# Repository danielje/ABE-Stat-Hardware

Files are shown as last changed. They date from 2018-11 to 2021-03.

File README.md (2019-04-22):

# ABE-Stat-Hardware
ABE-Stat Hardware Design / Assembly Files
For Android source code for wireless interface for device, go to https://github.com/danielje/ABE-Stat
For firmware source code (Arduino IDE) go to https://github.com/danielje/ABE-Stat-Arduino

Comprehensive documentation for the project is available in the open-source publication here: http://jes.ecsdl.org/content/166/9/B3056.short This set of files is referred to as "Files S1" in the manuscript above.

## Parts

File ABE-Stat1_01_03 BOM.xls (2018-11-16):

 | Bill of Materials for pc board: "ABE-Stat 1_01_03" as of: 5/11/2018 12 PM
Ref | Item | Quantity | for 50 | w overage | Designator | Description | Value | Package | Type | Manufacturer | Mfctr. Part Number | Distributor | Dstbr. Part # | Cost Each | Total parts cost | Incl. In Kit | Need for Build | Qty. To Return | Comments
PSTAT1 | 1 | 1 | 50 | 60 | A1 | ESP8266 WiFi Module |  |  |  | Esspressif | ESP-12S | Adafruit; Electrodragon | ESP-12S | $2.00 |  | ($2 from electrodragon; $6.95 from Adafruit)
PSTAT2 | 2 | 1 | 50 | 60 | A2 | MODULE BLUETOOTH V2.1+EDR |  |  | smt | Microchip Technology (http://digikey.com/Suppliers/us/Microchip-Technology.page?lang=en) | RN-42 | Digikey | 740-1038-1-ND | $15.44 | $15.44
PSTAT3 | 3 | 17 | 850 | 950 | C1 - C17 | CAP CER 0.1UF 16V X7R 0805 | 0.1 uF | 0805 | smt | Johanson Dielectrics Inc. | 160R15W104KV4T | Digikey | 709-1183-1-ND | $0.06 | $0.94
PSTAT4 | 4 | 9 | 450 | 550 | C18 - C26 | CAP CER 10UF 16V 20% X5R 0805 | 10 uF | 0805 | smt | TDK Corporation (http://digikey.com/Suppliers/us/TDK.page?lang=en) | C2012X5R1C106M085AC | Digikey | 445-7645-1-ND | $0.06 | $0.57
PSTAT5 | 5 | 4 | 200 | 300 | C27 - C30 | CAP CER 2200PF 50V X7R 0805 | 2200pF | 0806 | smt | KEMET (https://www.digikey.com/en/supplier-centers/k/kemet) | C0805C222K5RACTU | Digikey | 399-1151-1-ND | $0.01
PSTAT6 | 6 | 3 | 150 | 250 | C31 - C33 | CAP CER 10000PF 16V X7R 0805 | 10000 pF | 0805 | smt | KEMET | C0805C103K4RACTU | Digikey | 399-7995-1-ND | $0.03 | $0.10
PSTAT7 | 7 | 3 | 150 | 250 | C34 - C36 | CAP CER 4.7UF 10V X7R 0805 | 4.7 uF | 0805 | smt | TDK Corporation | C2012X7R1A475M085AC | Digikey | 445-14528-1-ND | $0.08 | $0.23
PSTAT8 | 8 | 2 | 100 | 200 | C37, C38 | CAP CER 0.22UF 16V X7R 0805 | 0.22 uF | 0805 | smt | Yageo | CC0805JRX7R7BB224 | Digikey | 311-4267-1-ND | $0.04 | $0.08
PSTAT9 | 9 | 1 | 50 | 150 | C39 | CAP CER 10PF 50V C0G/NP0 0805 | 10 pF | 0805 | smt | KEMET | C0805C100J5GACAUTO | Digikey | 399-6914-1-ND | $0.02 | $0.02
PSTAT10 | 10 | 1 | 50 | 75 | C40 | CAP ALUM POLY 47UF 20% 6.3V SMD | 47 uF | 7343 | smt | Panasonic Electronic Components (https://www.digikey.com/en/supplier-centers/p/panasonic) | EEF-CD0J470R | Digikey | PCE3160CT-ND | $0.53 | $0.53
PSTAT11 | 11 | 2 | 100 | 200 | D1, D2 | DIODE SCHOTTKY 40V 1A SOD123 |  | SOD123 | smt | Nexperia USA Inc. (https://www.digikey.com/en/supplier-centers/n/nexperia) | PMEG4010CEGWX | Digikey | 1727-7337-1-ND | $0.12 | $0.24
PSTAT12 | 12 | 6 | 300 | 400 | FB1 - FB3 | FERRITE BEAD 1.5 KOHM 0805 1LN |  | 0805 | smt | Wurth Electronics Inc. (https://www.digikey.com/en/supplier-centers/w/wurth-electronics) | 742792097 | Digikey | 732-4649-1-ND | $0.19 | $1.16
PSTAT13 | 13 | 1 | 50 | 60 | J1 | CONN TERM BLK 5POS 2.5MM SMD |  |  | smt | Phoenix Contact (https://www.digikey.com/en/supplier-centers/p/phoenix-contact) | 1771127 | Digikey | 277-2075-1-ND | $0.93 | $0.93
PSTAT14 | 14 | 1 | 50 | 60 | J2 | CONN TERM BLK 2POS 2.5MM SMD |  |  | smt | Phoenix Contact (https://www.digikey.com/en/supplier-centers/p/phoenix-contact) | 1771091 | Digikey | 277-2072-1-ND | $0.65 | $0.65
PSTAT15 | 15 | 1 | 50 | 60 | J3 | CONN RCPT USB MICRO B R/A SMT |  |  | smt | Wurth Electronics Inc. (https://www.digikey.com/en/supplier-centers/w/wurth-electronics) | 629105136821 | Digikey | 732-3155-1-ND | $1.11 | $1.11
PSTAT16 | 16 | 1 | 50 | 60 | J4 | CONN HEADER PH SIDE 2POS 2MM SMD |  |  | smt | JST Sales America Inc. | S2B-PH-SM4-TB(LF)(SN) | Digikey | 455-1749-1-ND | $0.42
PSTAT17 | 17 | 1 | 50 | 60 | J5 | 06 SIL VERT SMT HDR 450/RL |  |  | smt | Harwin Inc. | M20-8770642R | Digikey | 952-3487-1-ND | $0.52 | $0.52
PSTAT18 | 18 | 2 | 100 | 120 | LED1, LED2 | LED RED CLEAR 1206 SMD |  | 1206 | smt | QT Brightek (QTB) (https://www.digikey.com/en/supplier-centers/q/qt-brightek) | QBLP651-R | Digikey | 1516-1172-1-ND | $0.22 | $0.43
PSTAT19 | 19 | 1 | 50 | 60 | LED3 | LED RGB CLEAR 1411 SMD |  |  | smt | Wurth Electronics Inc (http://www.digikey.com/Suppliers/us/Wurth-Electronics.page?lang=en) | 150141M173100 | DigiKey | 732-4998-1-ND | $0.60 | $0.60
PSTAT20 | 20 | 5 | 250 | 275 | Q1 - Q5 | MOSFET N-CH 50V 220MA SOT-23 |  | SOT-23-3 | smt | Fairchild Semiconductor (http://digikey.com/Suppliers/us/Fairchild-Semiconductor.page?lang=en) | BSS138 | Digikey | BSS138CT-ND | $0.04 | $0.21
PSTAT21 | 21 | 1 | 50 | 75 | Q6 | MOSFET P-CH 50V 130MA SOT323 |  | SOT-23-3 | smt | Diodes Incorporated | BSS84W-7-F | Digikey | BSS84W-FDICT-ND | $0.12 | $0.12
PSTAT22 | 22 | 3 | 150 | 175 | Q7 - Q9 | MOSFET P-CH 8V 1.4A SOT-323 |  |  |  | ON Semiconductor | NTS2101PT1G | Digikey | NTS2101PT1GOSCT-ND | $0.17 | $0.50
PSTAT23 | 23 | 20 | 1000 | 1100 | R1 - R20 | RES 10K OHM 1/8W 5% 0805 SMD | 10 k | 0805 | smt | Panasonic Electronic Components (http://digikey.com/Suppliers/us/Panasonic-Electronic-Components.page?lang=en) | ERJ-6GEYJ103V | Digikey | P10KACT-ND | $0.00448 | #REF!
PSTAT24 | 24 | 6 | 300 | 400 | R20 - R26 | RES SMD 1K OHM 5% 1/8W 0805 | 1 k | 0805 | smt | Panasonic Electronic Components (http://digikey.com/Suppliers/us/Panasonic-Electronic-Components.page?lang=en) | ERJ-6GEYJ102V | Digikey | P1.0KACT-ND | $0.0041
PSTAT25 | 25 | 4 | 200 | 300 | R27 - R30 | RES SMD 22K OHM 5% 1/8W 0805 | 22k | 0805 | smt | Panasonic Electronic Components (http://digikey.com/Suppliers/us/Panasonic-Electronic-Components.page?lang=en) | ERJ-6GEYJ223V | Digikey | P22KACT-ND | $0.0041
PSTAT26 | 26 | 4 | 200 | 300 | R31 - R34 | RES SMD 100K OHM 0.1% 1/8W 0805 | 100k | 0805 | smt | Panasonic Electronic Components | ERA-6AEB104V | Digikey | P100KDACT-ND | $0.05
PSTAT27 | 27 | 3 | 150 | 250 | R35 - R37 | RES SMD 3.3K OHM 5% 1/8W 0805 | 3.3k | 0805 | smt | Panasonic Electronic Components (http://digikey.com/Suppliers/us/Panasonic-Electronic-Components.page?lang=en) | ERJ-6GEYJ332V | Digikey | P3.3KACT-ND | $0.0041
PSTAT28 | 28 | 3 | 150 | 250 | R38 - R40 | RES SMD 10K OHM 0.1% 1/8W 0805 | 10k | 0805 | smt | Panasonic Electronic Components | ERA-6AEB103V | Digikey | P10KDACT-ND | $0.05
PSTAT29 | 29 | 2 | 100 | 200 | R41, R42 | RES SMD 1M OHM 0.1% 1/8W 0805 | 1M | 0805 | smt | Panasonic Electronic Components | ERA-6AEB105V | Digikey | P1MDACT-ND | $0.05
PSTAT30 | 30 | 2 | 100 | 200 | R43, R44 | RES SMD 100 OHM 5% 1/8W 0805 | 100W | 0805 | smt | Panasonic Electronic Components (http://digikey.com/Suppliers/us/Panasonic-Electronic-Components.page?lang=en) | ERJ-6GEYJ101V | Digikey | P100ACT-ND | $0.0041
PSTAT31 | 31 | 1 | 50 | 150 | R45 | RES SMD 1K OHM 0.1% 1/8W 0805 | 1k | 0805 | smt | Panasonic Electronic Components (https://www.digikey.com/en/supplier-centers/p/panasonic) | ERA-6AEB102V | Digikey | P1.0KDACT-ND | $0.05
PSTAT32 | 32 | 1 | 50 | 150 | R46 | RES SMD 2K OHM 5% 1/8W 0805 | 2k | 0805 | smt | Panasonic Electronic Components (https://www.digikey.com/en/supplier-centers/p/panasonic) | ERJ-6GEYJ202V | Digikey | P2.0KACT-ND | $0.01
PSTAT33 | 33 | 1 | 50 | 150 | R47 | RES SMD 33K OHM 5% 1/8W 0805 | 33k | 0805 | smt | Panasonic Electronic Components (https://www.digikey.com/en/supplier-centers/p/panasonic) | ERJ-6GEYJ333V | Digikey | P33KACT-ND | $0.0041
PSTAT34 | 34 | 1 | 50 | 100 | R48 | RES SMD 2 OHM 5% 1W 2512 | 2W | 2512 | smt | Panasonic Electronic Components (https://www.digikey.com/en/supplier-centers/p/panasonic) | ERJ-1TYJ2R0U | Digikey | PT2.0XCT-ND | $0.07
PSTAT35 | 35 | 3 | 150 | 160 | S1 - S3 | SWITCH PUSH SPST-NO 0.1A 35V |  |  | smt | RAFI USA (https://www.digikey.com/en/supplier-centers/r/rafi) | 1.14002.1010000 | Digikey | 1.14002.1010000CT-ND | $0.06
PSTAT36 | 36 | 1 | 50 | 60 | SH1 | BOARD LEVEL EMI SHIELD 1.15"x2.9"x0.1" |  |  | smt | Orbel | G-1.15SA2.9-0.1ZC | Orbel | G-1.15SA2.9-0.1ZC | $5.00 | $5.00
PSTAT37 | 37 | 1 | 50 | 60 | U1 | IC CONTROLLR LI-ION 4.2V SOT23-5 |  | SOT23-5 | smt | Microchip Technology (https://www.digikey.com/en/supplier-centers/m/microchip-technology) | MCP73831T-2ACI/OT | Digikey | MCP73831T-2ACI/OTCT-ND | $0.43
PSTAT38 | 38 | 1 | 50 | 60 | U2 | IC REG LDO 3.3V 0.6A SOT-2233L |  | SOT-2233L | smt | Diodes Incorporated (https://www.digikey.com/en/supplier-centers/d/diodes) | AP7365-33EG-13 | Digikey | AP7365-33EG-13DICT-ND | $0.39
PSTAT39 | 39 | 1 | 50 | 60 | U3 | IC VREF SERIES 3.3V SOT23-3 | 3.3V | SOT-23-3 | smt | Intersil (https://www.digikey.com/en/supplier-centers/i/intersil) | ISL60002BAH333Z-T7A | Digikey | ISL60002BAH333Z-T7ACT-ND | $4.72
PSTAT40 | 40 | 1 | 50 | 60 | U4 | IC VREF GND REF ADJ 8SOIC |  | 8SOIC | smt | Texas Instruments | TLE2426IDR | Digikey | 296-1345-1-ND | $0.79
PSTAT41 | 41 | 2 | 100 | 110 | U5, U6 | IC SHIFT REGISTER 8-BIT 16-TSSOP |  | 16-TSSOP | smt | Fairchild/ON Semiconductor (https://www.digikey.com/en/supplier-centers/f/fairchild) | MM74HC595MTCX | Digikey | MM74HC595MTCXCT-ND | $0.15
PSTAT42 | 42 | 2 | 100 | 110 | U7, U8 | IC MUX/DEMUX 2X1 8VSSOP |  | 8VSSOP | smt | Nexperia USA Inc. (https://www.digikey.com/en/supplier-centers/n/nexperia) | 74LVC1G53DC,125 | Digikey | 1727-3492-1-ND | $0.17
PSTAT43 | 43 | 2 | 100 | 110 | U9, U10 | IC SWITCH SPDT SC70-6 |  | SC-70-6 | smt | Analog Devices Inc. (https://www.digikey.com/en/supplier-centers/a/analog-devices) | ADG779BKSZ-REEL7 | Digikey | ADG779BKSZ-REEL7CT-ND | $1.00
PSTAT44 | 44 | 1 | 50 | 60 | U11 | NETWORK ANALYZER 12B 1MSP 16SSOP |  | 16SSOP | smt | Analog Devices Inc. | AD5933YRSZ-REEL7 | Digikey | AD5933YRSZ-REEL7CT-ND | $34.16
PSTAT45 | 45 | 1 | 50 | 60 | U12 | IC ADC 24-BIT 2KSPS 16-TSSOP |  | 16-TSSOP | smt | Analog Devices Inc. | ADS1220IPWR | Digikey | 296-39851-1-ND | $7.87
PSTAT46 | 46 | 1 | 50 | 60 | U13 | IC DAC 16BIT SPI/SRL SOT23-8 |  | SOT23-8 | smt | Analog Devices Inc. | AD5061BRJZ-2REEL7 | Digikey | AD5061BRJZ-2REEL7CT-ND | $6.40
PSTAT47 | 47 | 1 | 50 | 60 | U14 | IC SWITCH OCTAL SPST 24TSSOP |  | 24TSSOP | smt | Analog Devices Inc. | ADG715BRUZ | Digikey | ADG715BRUZ-REEL7CT-ND | $5.20
PSTAT48 | 48 | 1 | 50 | 60 | U15 | IC GATE XOR 2CH 2-INP US8 | XOR | US8 | smt | Texas Instruments (http://digikey.com/Suppliers/us/Texas-Instruments.page?lang=en) | SN74LVC2G86DCUR | Digikey | 296-13275-1-ND | $0.28 | $0.84
PSTAT49 | 49 | 1 | 50 | 60 | U16 | IC MULTIPLEXER 4X1 10USOIC |  | 10USOIC | smt | Analog Devices Inc. | ADG704BRMZ | Digikey | ADG704BRMZ-REELCT-ND | $1.41
PSTAT50 | 50 | 1 | 50 | 60 | U17 | IC AMP PREC 3FA BIAS CURR 8SOIC |  | 8SOIC | smt | Texas Instruments (http://digikey.com/Suppliers/us/Texas-Instruments.page?lang=en) | LMP7721MA/NOPB | Digikey | LMP7721MA/NOPB-ND | $5.29 | $10.57
PSTAT51 | 51 | 3 | 150 | 160 | U18 - U20 | IC OPAMP GP 2.5MHZ RRO 8VSSOP |  | 8-MSOP | smt | Texas Instruments | LMP7702MM/NOPB | Digikey | LMP7702MM/NOPBCT-ND | $2.61
PSTAT52 | 52 | 2 | 100 | 110 | U21, U22 | IC OPAMP GP 17MHZ RRO SOT23-5 |  | SOT23-5 | smt | Texas Instruments | LMP7715MF/NOPB | Digikey | LMP7715MF/NOPBCT-ND | $1.22
PSTAT53 | 53 | 1 | 50 | 60 | X1 | OSC MEMS 250.0000KHZ CMOS SMD | 250kHz | 4-SMD | smt | Microchip Technology | DSC6083CI2A-250K000 | Digikey | DSC6083CI2A-250K000T-ND | $0.69
 |  | 142

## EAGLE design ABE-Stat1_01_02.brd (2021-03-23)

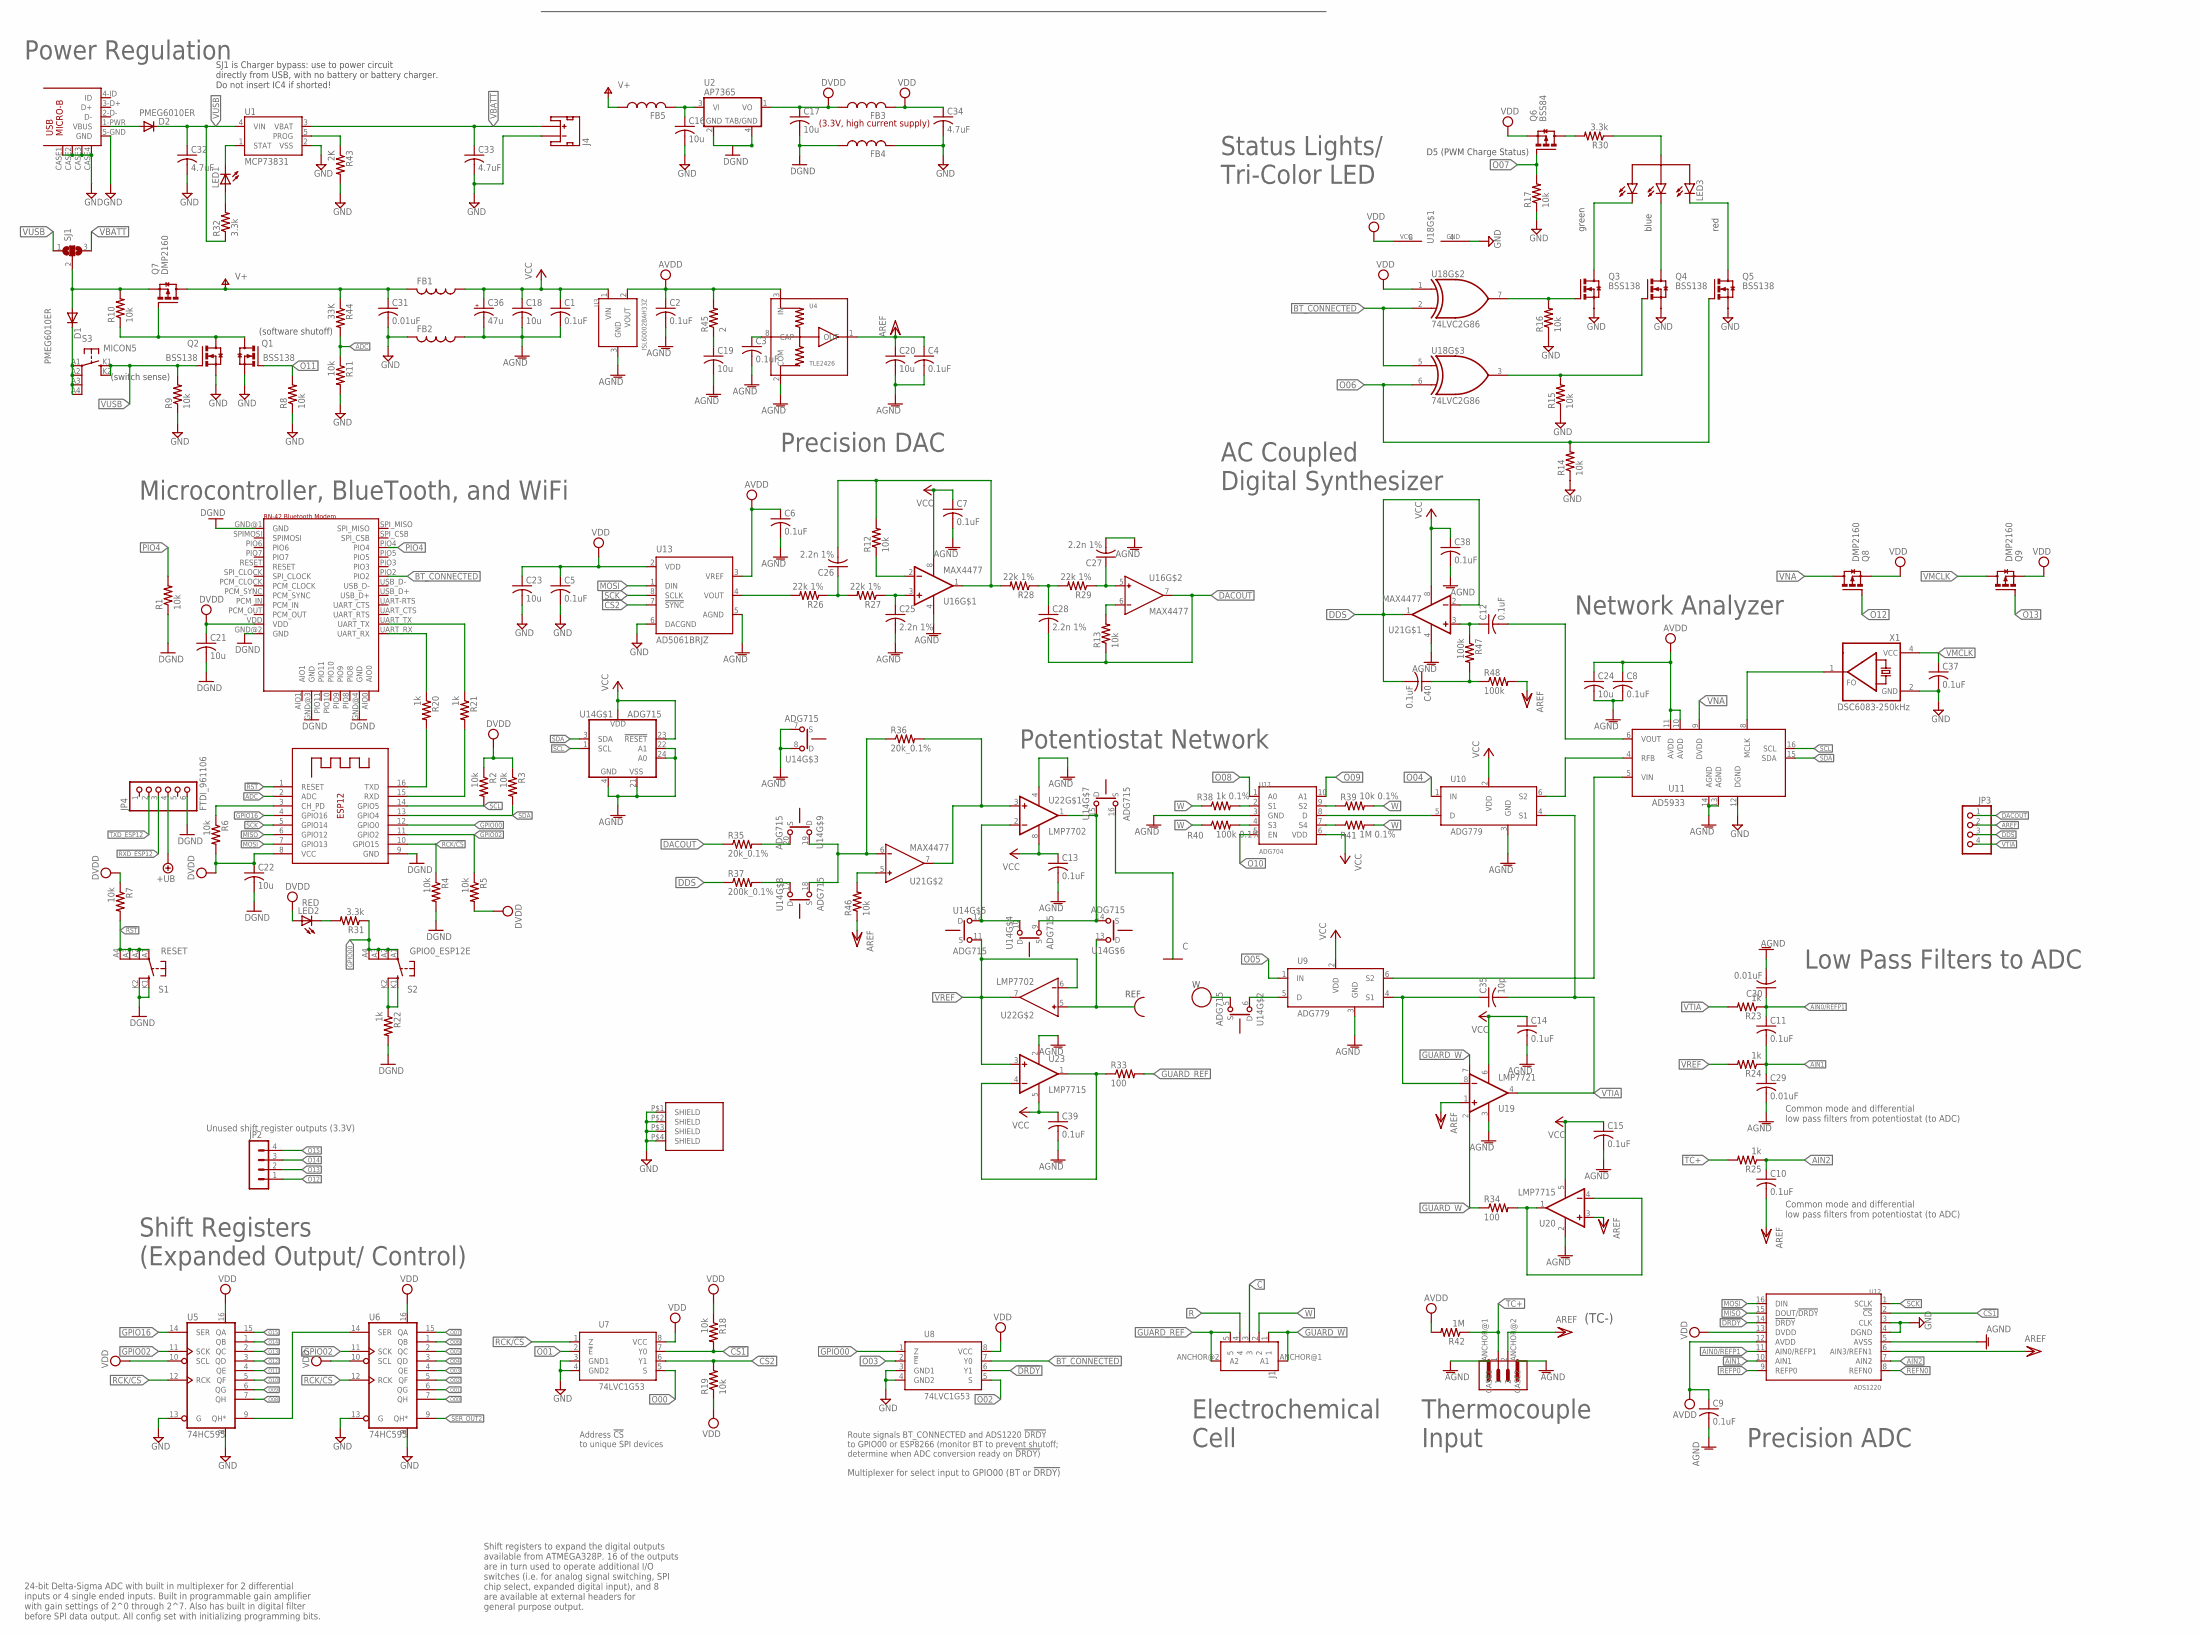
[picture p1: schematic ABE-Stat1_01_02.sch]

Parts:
A1: ESP-12E; ESP-12
A2: RN-42_BLUETOOTH; RN-42
C1, C2, C3, C4, C5, C6, C7, C8, C9, C10, C11, C12, C13, C14, C15, C37, C38, C39, C40: 0.1uF; C0805
C16, C17, C18, C19, C20, C21, C22, C23, C24: 10u; C0805
C25, C26, C27, C28: 2.2n 1%; C0805
C29, C30, C31: 0.01uF; C0805
C32, C33, C34: 4.7uF; C0805
C35: 10p; C0805
C36: 47u; D/7343-31W
D1, D2: PMEG6010ER; DIODE_SOD123
FB1, FB2, FB3, FB4, FB5: FERRITE_BEAD_5A_0805; R0805
J1: 5-PIN-VERTICAL-PHOENIX_2.5MM-SMD; 5-PIN-VERT_PHOENIX_SMD
J2: 1A_JENKINS_2013_2PIN_SMD_PHOENIX_CONTACTVERTICAL; 2-PIN-VERT_PHOENIX_SMD
J3: USB-MICRO-B; USB_MICRO_B_WURTH_629105136821
J4: JST_2MM_MALE; JST-2-SMD
JP2: MA04-1
JP3: PINHD-1X4; 1X04
JP4: FTDI_961106; 6_PIN_0.1IN_STRAIGHT_HEADER
LED1: LEDCHIPLED_1206; CHIPLED_1206
LED2: RED; LED-1206
LED3: LED_RBG_COM_ANODE; LED_RGB_WURTH_150141M173100
Q1, Q2, Q3, Q4, Q5: BSS138; SOT-23
Q6: BSS84; SOT-23-3
Q7, Q8, Q9: DMP2160; SOT-23-3
R1, R2, R3, R4, R5, R6, R7, R8, R9, R10, R11, R12, R13, R14, R15, R16, R17, R18, R19, R46: 10k; R0805
R20, R21, R22, R23, R24, R25: 1k; R0805
R26, R27, R28, R29: 22k 1%; R0805
R30, R31, R32: 3.3k; R0805
R33, R34: 100; R0805
R35, R36: 20k_0.1%; R0805
R37: 200k_0.1%; R0805
R38: 1k 0.1%; R0805
R39: 10k 0.1%; R0805
R40: 100k 0.1%; R0805
R41: 1M 0.1%; R0805
R42: 1M; R0805
R43: 2K; R0805
R44: 33K; R0805
R45: 2; R2512
R47, R48: 100k; R0805
S1: RESET; RAFI-MICON5_SWITCH
S2: GPIO0_ESP12E; RAFI-MICON5_SWITCH
S3: MICON5; RAFI-MICON5_SWITCH
SH1: SMARTDART_SHIELD; SMARTDART-SHIELD
SJ1: SJ2W; SJ_2
U1: MCP73831; SOT23-5
U2: AP7365; SOT-223
U3: ISL60002BAH33Z; SOT-23-3
U4: TLE2426; SOIC-8
U5, U6: 74HC595; TSSOP16
U7, U8: 74LVC1G53; VSSOP8
U9, U10: ADG779; SC70-6
U11: AD5933; SSOP-16
U12: ADS1220; TSSOP16
U13: AD5061BRJZ; SOT-23-8
U14: ADG715; TSSOP24
U16, U21: MAX4477; UMAX8
U17: ADG704; MSOP10
U18: 74LVC2G86; US-8
U19: LMP7721; SOIC-8
U20, U23: LMP7715; SOT23-5
U22: LMP7702; MSOP8
X1: DSC6083-250kHz; DSC60XX_OSCILLATOR_3.2X2.5MM

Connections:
!CS1: R18.2, U7.7 (Y0), U12.2 (!CS)
!CS2: R19.2, U7.6 (Y1), U13.7 (!SYNC)
!DRDY: U8.6 (Y1), U12.14 (!DRDY)
!RST: A1.1 (RESET), R7.2, S1.A1, S1.A2 (P1), S1.A3 (P2), S1.A4 (P3)
+UB: JP4.4
AD5933_VIN: U9.6 (S2), U11.5 (VIN)
ADC: A1.2 (ADC), R11.1, R44.2
AGND: C1.2, C2.2, C3.2, C4.2, C6.2, C7.2, C8.2, C9.2, C13.2, C14.2, C15.2, C18.2, C19.2, C20.2, C24.2, C25.2, C27.2, C29.2, C30.2, C36.-, C38.2, C39.2, FB2.1, J2.ANCHOR@1 (CASE1), J2.ANCHOR@2 (CASE2), U3.3 (GND), U4.2 (COM), U9.3 (GND), U10.3 (GND), U11.13 (AGND), U11.14 (AGND), U12.5 (AVSS), U13.5 (AGND), U14.4 (GND), U14.7 (S), U14.8 (D), U14.21 (VSS), U14.22 (A1), U14.24 (A0), U16.4 (V-), U17.3 (GND), U19.3 (V-), U20.2 (V-), U21.4 (V-), U22.4 (V-), U23.2 (V-)
AIN0/REFP1: C11.1, C30.1, R23.1, U12.11 (AIN0/REFP1)
AIN1: C11.2, C29.1, R24.1, U12.10 (AIN1)
AIN2: C10.1, R25.1, U12.7 (AIN2)
AREF: C4.1, C10.2, C20.1, J2.2, JP3.2, R46.1, R48.2, U4.1 (OUT), U12.6 (AIN3/REFN1), U19.1 (+IN), U20.3 (+IN)
AVDD: C2.1, C6.1, C8.1, C9.1, C24.1, R42.2, R45.2, U3.2 (VOUT), U4.3 (IN), U11.10 (AVDD), U11.11 (AVDD), U12.12 (AVDD), U13.3 (VREF)
BT_CONNECTED: A2.PIO2, U8.7 (Y0), U18.2 (I1), U18.5 (I0)
C: J1.3, U14.16 (S)
DACOUT: C28.2, JP3.1, R13.1, R35.1, U16.7 (OUT)
DDS: C40.2, JP3.3, R37.1, U21.1 (OUT), U21.2 (-IN)
DGND: A1.9 (GND), A2.GND@1 (GND), A2.GND@2 (GND), A2.GND@3 (GND), A2.GND@4 (GND), C17.2, C21.2, C22.2, FB4.1, JP4.6, R1.1, R4.2, R22.2, S1.K1 (S), S1.K2 (S1), U2.2 (GND), U2.4 (GND1)
DVDD: A1.8 (VCC), A2.VDD, C17.1, C21.1, C22.1, FB3.1, LED2.A, R2.1, R3.1, R5.2, R6.2, R7.1, U2.1 (VO)
GND: C5.2, C16.2, C23.2, C31.2, C32.2, C33.2, C34.2, C37.2, FB2.2, FB4.2, J3.5-GND (GND), J3.CASE1 (CASE), J3.CASE2 (CASE), J3.CASE3 (CASE), J3.CASE4 (CASE), J4.1 (-), Q1.2-S (S), Q2.2-S (S), Q3.2-S (S), Q4.2-S (S), Q5.2-S (S), R8.1, R9.1, R11.2, R14.1, R15.1, R16.1, R17.1, R43.2, SH1.P$1, SH1.P$2, SH1.P$3, SH1.P$4, U1.2 (VSS), U5.8 (GND), U5.13 (G), U6.8 (GND), U6.13 (G), U7.3 (GND1), U7.4 (GND2), U8.3 (GND1), U8.4 (GND2), U11.12 (DGND), U12.3 (CLK), U12.4 (DGND), U13.6 (DACGND), U18.4 (GND), X1.2 (GND)
GPIO00: A1.12 (GPIO0), R31.1, S2.A1, S2.A2 (P1), S2.A3 (P2), S2.A4 (P3), U8.1 (Z)
GPIO02: A1.11 (GPIO2), R5.1, U5.11 (SCK), U6.11 (SCK)
GPIO16: A1.4 (GPIO16), U5.14 (SER)
GUARD_REF: J1.5, J1.ANCHOR@2 (A2), R33.2
GUARD_W: J1.1, J1.ANCHOR@1 (A1), R34.1, U19.2 (GUARD), U19.7 (GUARD)
MISO: A1.6 (GPIO12), U12.15 (DOUT/!DRDY)
MOSI: A1.7 (GPIO13), U12.16 (DIN), U13.1 (DIN)
unnamed: A2.UART_RX, R20.1
unnamed: U14.10 (D), U14.12 (D), U22.2 (-IN)
unnamed: D2.A, J3.1-PWR (VBUS)
unnamed: A2.UART_TX, R21.1
unnamed: Q3.1-G (G), R16.2, U18.7 (O)
unnamed: U9.5 (D), U14.6 (D)
unnamed: R43.1, U1.5 (PROG)
unnamed: U5.9 (QH*), U6.14 (SER)
unnamed: C25.1, R27.1, U16.3 (+IN)
unnamed: LED1.C, U1.1 (STAT)
unnamed: R26.2, U13.4 (VOUT)
unnamed: LED1.A, R32.2
unnamed: C19.1, R45.1
unnamed: R37.2, U14.17 (D)
unnamed: C26.1, R26.1, R27.2
unnamed: R22.1, S2.K1 (S), S2.K2 (S1)
unnamed: Q4.1-G (G), R15.2, U18.3 (O)
unnamed: D1.C, S3.A1, S3.A2 (P1), S3.A3 (P2), S3.A4 (P3)
unnamed: C3.1, U4.8 (CAP)
unnamed: C26.2, R12.2, R28.2, U16.1 (OUT)
unnamed: C28.1, R28.1, R29.2
unnamed: C27.1, R29.1, U16.5 (IN+)
unnamed: R12.1, U16.2 (-IN)
unnamed: U14.9 (S), U14.14 (S), U14.15 (D), U22.1 (OUT)
unnamed: R13.2, U16.6 (IN-)
unnamed: LED2.C, R31.2
unnamed: C35.1, U9.4 (S1), U19.8 (-IN)
unnamed: R36.1, U14.18 (S), U14.19 (D), U21.6 (IN-)
unnamed: R36.2, U21.7 (OUT), U22.3 (+IN)
unnamed: U10.6 (S2), U11.4 (RFB)
unnamed: R41.1, U17.7 (S4)
unnamed: R33.1, U23.1 (OUT), U23.4 (-IN)
unnamed: R39.1, U17.9 (S2)
unnamed: Q1.3-D (D), Q2.3-D (D), Q7.1 (G), R10.1
unnamed: U10.5 (D), U17.8 (D)
unnamed: R38.2, U17.2 (S1)
unnamed: R40.2, U17.4 (S3)
unnamed: LED3.G, Q3.3-D (D)
unnamed: R34.2, U20.1 (OUT), U20.4 (-IN)
unnamed: LED3.B, Q4.3-D (D)
unnamed: LED3.R, Q5.3-D (D)
unnamed: Q6.3 (D), R30.2
unnamed: LED3.A, R30.1
unnamed: R35.2, U14.20 (S)
unnamed: C16.1, FB5.2, U2.3 (VI)
unnamed: A1.3 (CH_PD), R6.1
unnamed: U11.8 (MCLK), X1.1 (FO)
unnamed: D1.A, Q7.2 (S), R10.2, SJ1.2
unnamed: R46.2, U21.5 (IN+)
unnamed: C40.1, R47.2, R48.1
unnamed: C12.1, R47.1, U21.3 (+IN)
unnamed: C12.2, U11.6 (VOUT)
O00: U6.7 (QH), U7.5 (S)
O01: U6.6 (QG), U7.2 (!E)
O02: U6.5 (QF), U8.5 (S)
O03: U6.4 (QE), U8.2 (!E)
O04: U6.3 (QD), U10.1 (IN)
O05: U6.2 (QC), U9.1 (IN)
O06: Q5.1-G (G), R14.2, U6.1 (QB), U18.6 (I1)
O07: Q6.1 (G), R17.2, U6.15 (QA)
O08: U5.7 (QH), U17.1 (A0)
O09: U5.6 (QG), U17.10 (A1)
O10: U5.5 (QF), U17.5 (EN)
O11: Q1.1-G (G), R8.2, U5.4 (QE)
O12: JP2.1, Q8.1 (G), U5.3 (QD)
O13: JP2.2, Q9.1 (G), U5.2 (QC)
O14: JP2.3, U5.1 (QB)
O15: JP2.4, U5.15 (QA)
PIO4: A2.PIO4, R1.2
R: J1.4, U14.13 (D), U22.5 (IN+)
RCK/!CS: A1.10 (GPIO15), R4.1, U5.12 (RCK), U6.12 (RCK), U7.1 (Z)
REFN0: U12.8 (REFN0)
REFP0: U12.9 (REFP0)
RXD_ESP12: A1.15 (RXD), JP4.3, R21.2
SCK: A1.5 (GPIO14), U12.1 (SCLK), U13.8 (SCLK)
SCL: A1.14 (GPIO5), R2.2, U11.16 (SCL), U14.1 (SCL)
SDA: A1.13 (GPIO4), R3.2, U11.15 (SDA), U14.3 (SDA)
SER_OUT2: U6.9 (QH*)
TC+: J2.1, R25.2, R42.1
TXD_ESP12: A1.16 (TXD), JP4.2, R20.2
V+: C31.1, FB1.2, FB5.1, Q7.3 (D), R44.1
VBATT: C33.1, J4.2 (+), SJ1.3, U1.3 (VBAT)
VCC: C1.1, C7.1, C13.1, C14.1, C15.1, C18.1, C36.+, C38.1, C39.1, FB1.1, U3.1 (VIN), U9.2 (VDD), U10.2 (VDD), U14.2 (VDD), U14.23 (!RESET), U16.8 (V+), U17.6 (VDD), U19.6 (V+), U20.5 (V+), U21.8 (V+), U22.8 (V+), U23.5 (V+)
VDD: C5.1, C23.1, C34.1, FB3.2, Q6.2 (S), Q8.2 (S), Q9.2 (S), R18.1, R19.1, U5.10 (SCL), U5.16 (VCC), U6.10 (SCL), U6.16 (VCC), U7.8 (VCC), U8.8 (VCC), U12.13 (DVDD), U13.2 (VDD), U18.1 (I0), U18.8 (VCC)
VMCLK: C37.1, Q9.3 (D), X1.4 (VCC)
VNA: Q8.3 (D), U11.9 (DVDD)
VREF: R24.2, U14.11 (S), U22.6 (IN-), U22.7 (OUT), U23.3 (+IN)
VTIA: C35.2, JP3.4, R23.2, U10.4 (S1), U19.4 (OUT)
VUSB: C32.1, D2.C, Q2.1-G (G), R9.2, R32.1, S3.K1 (S), S3.K2 (S1), SJ1.1, U1.4 (VIN)
W: J1.2, R38.1, R39.2, R40.1, R41.2, U14.5 (S)

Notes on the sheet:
(3.3V, high current supply)
Route signals BT_CONNECTED and ADS1220 !DRDY to GPIO00 or ESP8266 (monitor BT to prevent shutoff; determine when ADC conversion ready on !DRDY)
Shift registers to expand the digital outputs available from ATMEGA328P. 16 of the outputs are in turn used to operate additional I/O switches (i.e. for analog signal switching, SPI chip select, expanded digital input), and 8 are available at external headers for general purpose output.
Multiplexer for select input to GPIO00 (BT or !DRDY)
Power Regulation
Microcontroller, BlueTooth, and WiFi
Precision ADC
Shift Registers (Expanded Output/ Control)
24-bit Delta-Sigma ADC with built in multiplexer for 2 differential inputs or 4 single ended inputs. Built in programmable gain amplifier with gain settings of 2^0 through 2^7. Also has built in digital filter before SPI data output. All config set with initializing programming bits.
Common mode and differential low pass filters from potentiostat (to ADC)
Address !CS to unique SPI devices
(switch sense)
(software shutoff)
Precision DAC
Network Analyzer
Potentiostat Network
Low Pass Filters to ADC
Thermocouple Input
Electrochemical Cell
D5 (PWM Charge Status)
green
blue
red
Status Lights/ Tri-Color LED
(TC-)
Unused shift register outputs (3.3V)
REF
SJ1 is Charger bypass: use to power circuit directly from USB, with no battery or battery charger. Do not insert IC4 if shorted!
AC Coupled Digital Synthesizer

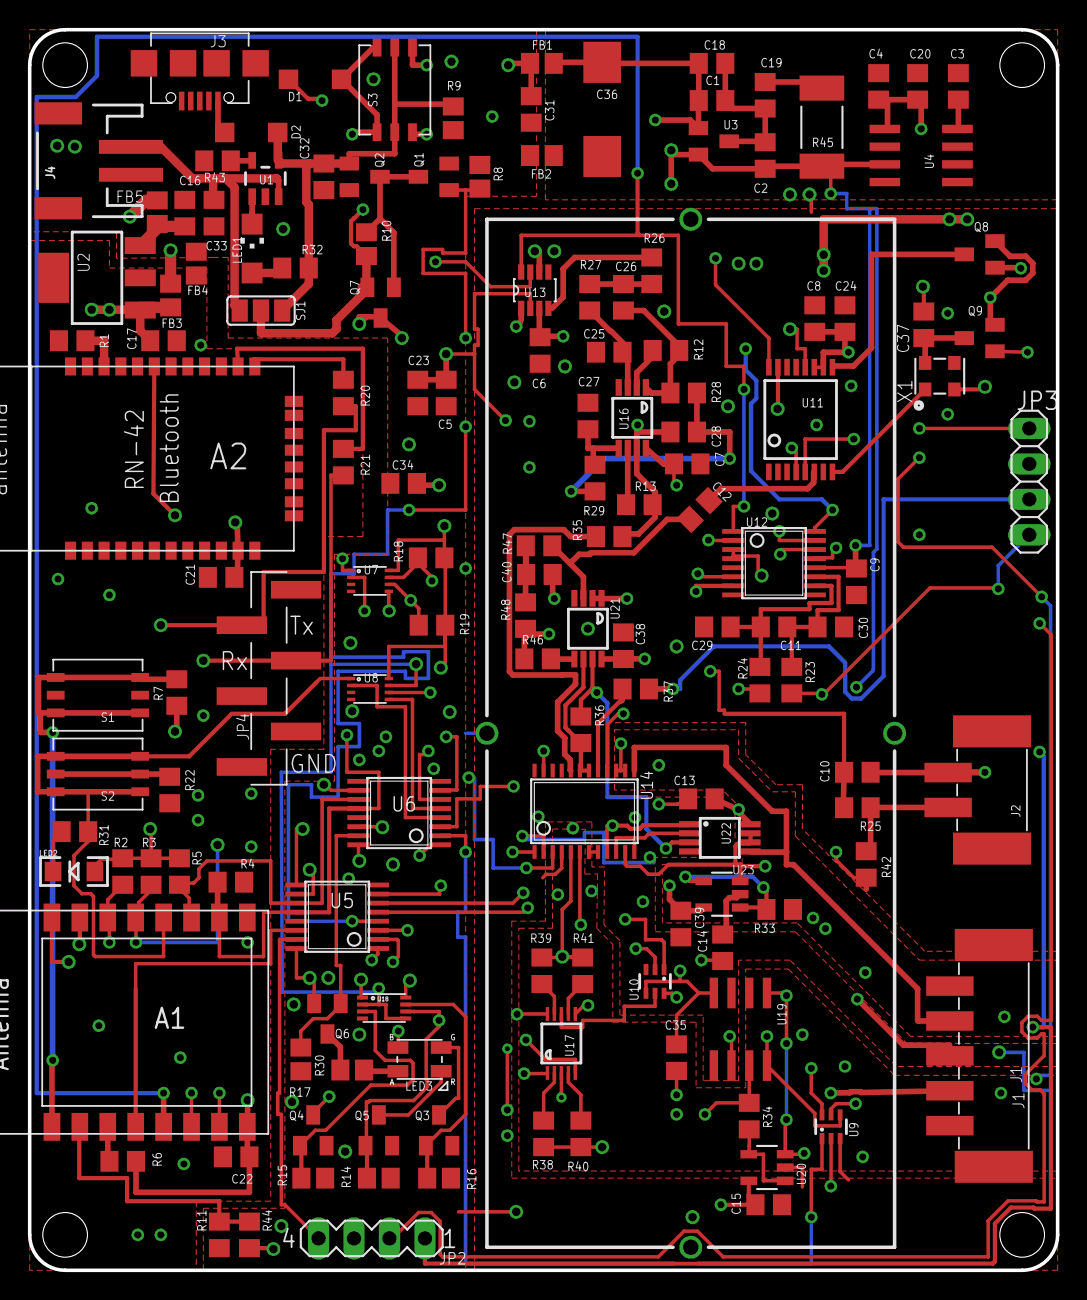
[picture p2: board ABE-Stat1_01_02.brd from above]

Board: 4 copper layers, 73.7 x 88.9 mm, 144 parts (0 on the bottom side), 113 nets.

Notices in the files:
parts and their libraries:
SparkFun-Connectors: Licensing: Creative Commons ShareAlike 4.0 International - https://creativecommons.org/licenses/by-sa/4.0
